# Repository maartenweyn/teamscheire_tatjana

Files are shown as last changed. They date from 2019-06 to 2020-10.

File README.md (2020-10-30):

# Team Scheire Tatjana - Tinnitus

Aflevering op VRTNu: [https://vrtnu.page.link/GqeyBG1gsRzztzNG9](https://vrtnu.page.link/GqeyBG1gsRzztzNG9)

Uitleg over de oplossing in deze podcast: [https://soundcloud.com/nerdlandmakertalk/09-maarten-weyn](https://soundcloud.com/nerdlandmakertalk/09-maarten-weyn)

# Geluidsmetingen

## 1. Wat is geluid?

**Geluid** is de **hoorbare verandering** van **luchtdruk** , of als je helemaal volledig wil zijn de verandering van de **dichtheid** van een **elastisch medium** , dat kan een **gas** zijn, een **vloeistof** of een **vaste** stof. En een geluidsbron veroorzaak verandering in de luchtdruk die zich in een golfbeweging door de lucht voortbewegen. Een luidspreker bijvoorbeeld zet een elektrisch signaal om in een beweging van een membraan. Die beweging zal dan een verandering in de luchtdruk veroorzaken.

Geluidsgolven tussen 20 Hz en 20 kHz, m.a.w. golven die 20 tot 20 000 keer per seconde bewegen kunnen door de mensen worden waargenomen. Boven 20 kHz hebben we wat we ultrasoon noemen.

Wist je dat geluid zich in lucht (bij 20°C en op zeeniveau) met ongeveer 343 m/s (of 1230 km/u) voortbeweegt, en in water van 20°C zelfs met 1482 m/s.

## 2. Wat is dan de geluidssterkte?

De **geluidsdruk** is het lokale drukverschil t.o.v. de atmosferische luchtdruk ten gevolge van een geluidsgolf. En dat wordt typisch in Pascal uitgedrukt.

Dit verschil wordt over een zeer kleine periode uitgemiddeld, men berekent de &quot;root mean square&quot; of de wortel van het gemiddelde van het kwadraat. Deze variatie is typisch zeer klein, de laagste waarde die nog hoorbaar is, is rond 2 \* 10-5 of 0.00002 Pa terwijl een explosie ongeveer 104 of 10000 kan zijn.

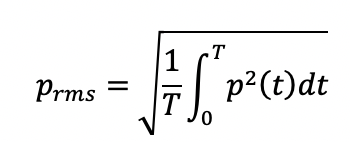
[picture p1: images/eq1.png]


Daarom gebruik met een logaritmes waarde om de geluidsruk uit te drukken en dat noemen het **geluidsniveau** of Sound Pressure Level (SPL) in dB:



Met p0 de referentieruk 2 x 10-5 Pa of 20 uPa, de gehoordrempel van een gemiddeld persoon bij een frequentie van 1000 Hz.

Dus deze waarde geeft een indicatie hoeveel keer het geluid luider is dan gehoordrempel.

## 3. Wat is een logaritme?

In het geval van een geluidsniveau wordt een logaritme gebruikt met grondtal 10. In dat geval is de logaritme van een getal het getal waartoe 10 moet worden verheven. de logaritme van 1000 is bijvoorbeeld 3 want 103 = 10 x 10 x 10 = 1000.

In het geval van het geluidsniveau berekenen we de logaritme van het aantal keer het geluid sterker is dan de gehoordrempel, en dat getal nog eens x 20.

## 4. Hoe kunnen we dat nu meten

We gaan dit meten met een MEMS microfoon. MEMS staat voor _microelectron-mechanical systems_ of hele kleine elektro-mechanische systemen. In een MEMS microfoon zit een zeer klein beweegbaar membraan, een klein gaatje (of meerdere) laten het toe dat de luchtdruk kan veranderen die door de geluidgolven worden veroorzaakt en een vaste structuur.

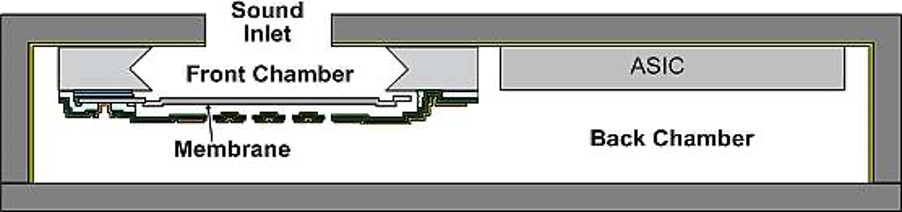
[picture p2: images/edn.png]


Diagram van een dwarssnede van een MEMS-microfoon (figuur van EDN)

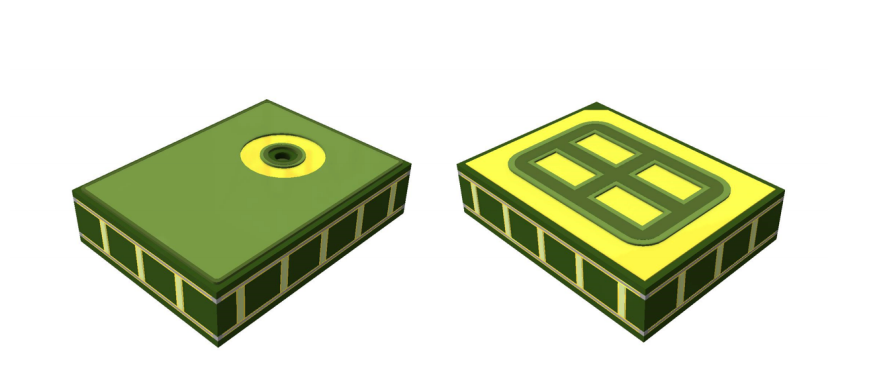
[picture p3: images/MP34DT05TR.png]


MP34DT05TR microfoon

Door de geluidgolven zal het membraan gaan bewegen en het verschil in capaciteit tussen het membraan en de vaste structuur wordt omgezet naar een elektrisch signaal.

In de chip van de MEMS-microfoon kan dit verschil in een spanning rechtstreeks worden doorgegeven naar een microcontroller (in analoge MEMS-microfoons) of in een digitale kan ze omgezet worden aar een PDM signaal.

Een PDM staat voor pulse density modulation. Bij PDM wordt een analoog signaal omgezet naar een binair signaal. In plaats van het signaal om te zetten naar codewoorden, komt bij PDM de relatieve dichtheid van de pulsen overeen met de amplitude van het analoge signaal.

0101101111111111111101101010010000000000000100010011011101111111111111011010100100000000000000100101

Vertegenwoordigd bvb



Figuur van Wikipedia (Kaldosh)

Het geluid wordt in dit geval 16000 keer per seconden gemeten. De microfoon is gekalibreerd en meet een waarde 1642 bij 94 dbA. Daarnaast meten we ook een root mean square gemiddelde in plaats van een dbFS (full scale meting) en we moeten dit nog corrigeren.

double leq = 3.0103+ 94 + 20 \* log10(sqrt(sumsquare / total\_samples) / 1642);

Nu voor we de samples gebruiken wordt de gemeten waarde nog gewogen naar de frequenties waarvoor het menselijk oor gevoeliger is. Zo worden bvb tonen onder de 1000 verzwakt. Een toon van 10 Hz wordt 70 keer zwakker gehoord dan een toon van 1000 Hz. Hoeveel dit niet helemaal correct is gebruiken we wel de dB(A) omdat de normen en wetgeving ook gebruik maakt van deze gewogen waarden.

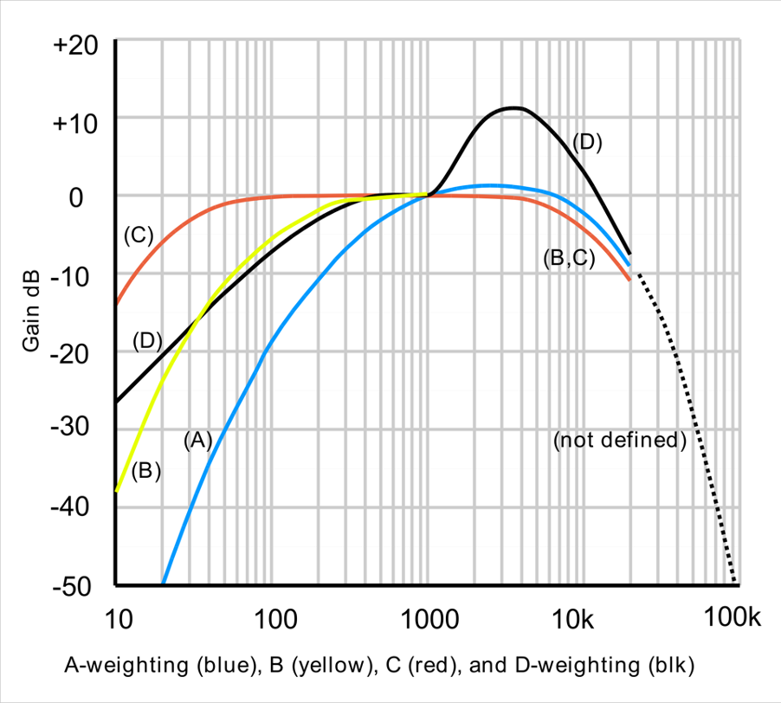
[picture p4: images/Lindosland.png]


Figuur van Lindosland at English Wikipedia

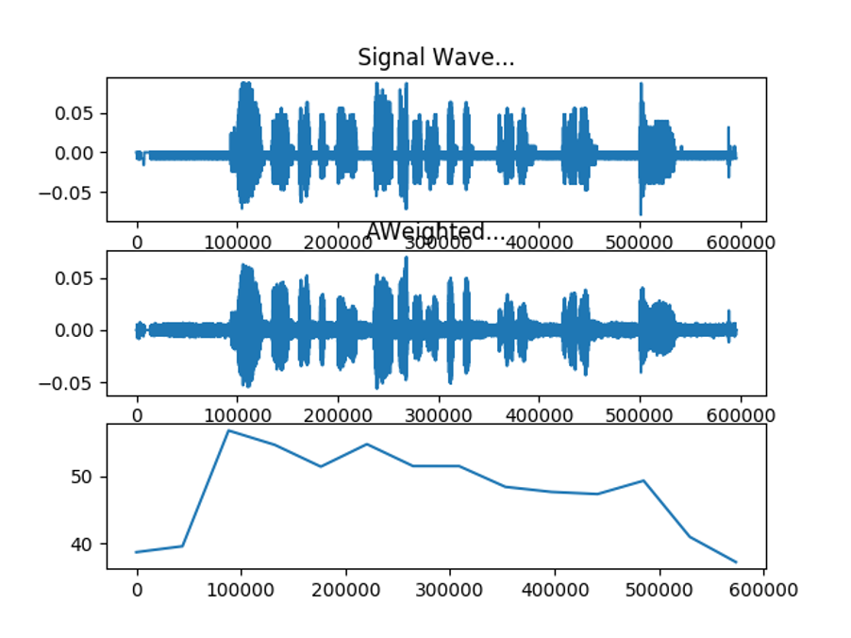
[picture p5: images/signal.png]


Nu kunnen we bijvoorbeeld per seconden meten wat het geluidsniveau is. Maar eigenlijk zijn we niet op zoek naar het geluidsniveau zelf, maar wel naar de geluidsdosis.

## 5. Wat is de geluidsdosis?

Een **geluidsdosis** is het gemiddelde geluidsniveau over een bepaalde (langere periode), bijvoorbeeld 8 uur of 24 uur. De WHO (wereld gezondheidsorganisatie) zegt dat deze normen voor 8u 80 dbA zijn en voor 24u 75 dbA.

Qua energieverbruik en dataopslag kunnen we uiteraard niet 8 u geluid gaan opnemen maar nemen we elke 10 seconden een sample van 1 seconde. Daarop bereken we het geluidsniveau. Daarna middelen we dit uit over 8u en 24u.

Je mag niet de gemiddeld van de dBA waarden nemen, dit zijn immers gemiddelde. Maar zetten de waardes eerst terug om naar de geluidsdruk en berekenen dan hoeveel % we reeds hebben ten opzichte van de herberekende waarde. Zo krijgen we 2 percentages die ook intuïtiever kunnen gebruikt worden door de gebruiker van het systeem.

# Wat staat er in de repo

* In **tizen** staat de oorspronkelijk ontwikkeling voor de Samsung Watch.
* In **hardware** het schema en PCB van de ontwikkelde wearble mee ontwikkeld door Kwinten Schram.
* In **3DModel** de stl van de gebruikte behuizing
* In **Arduino** een aantal test applicaties
* In **cordova** de cordova applicatie voor iOS
* In **Firmware** de code voor de wearable

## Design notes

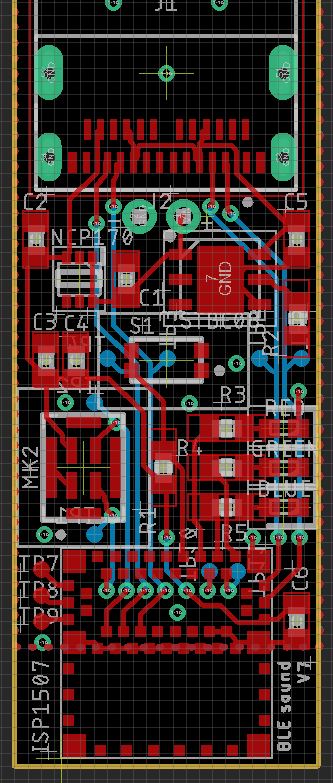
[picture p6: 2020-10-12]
hardware/brd1.JPG

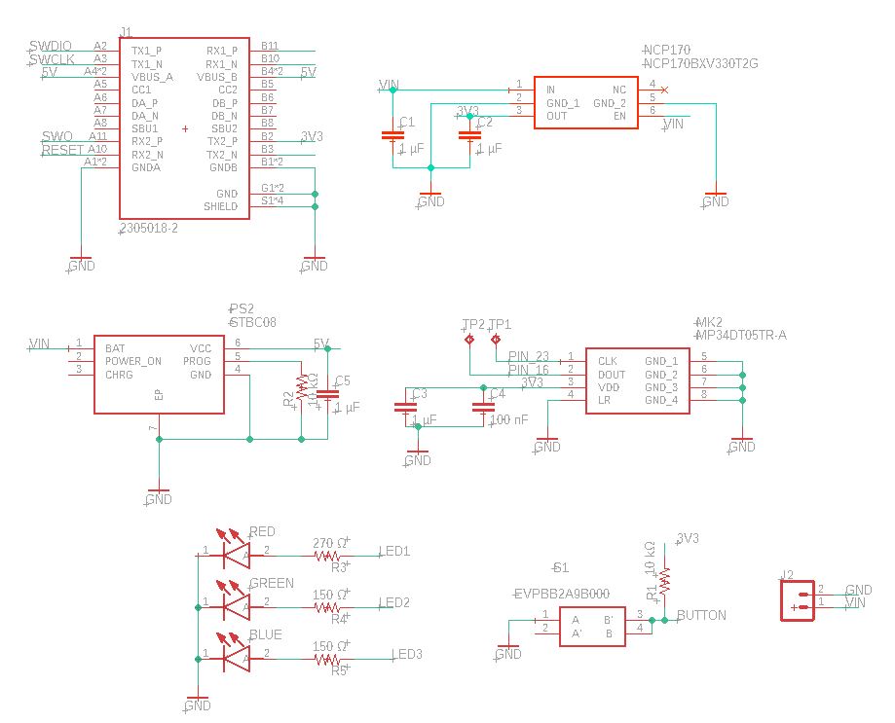
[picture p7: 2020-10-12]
hardware/sch1.JPG

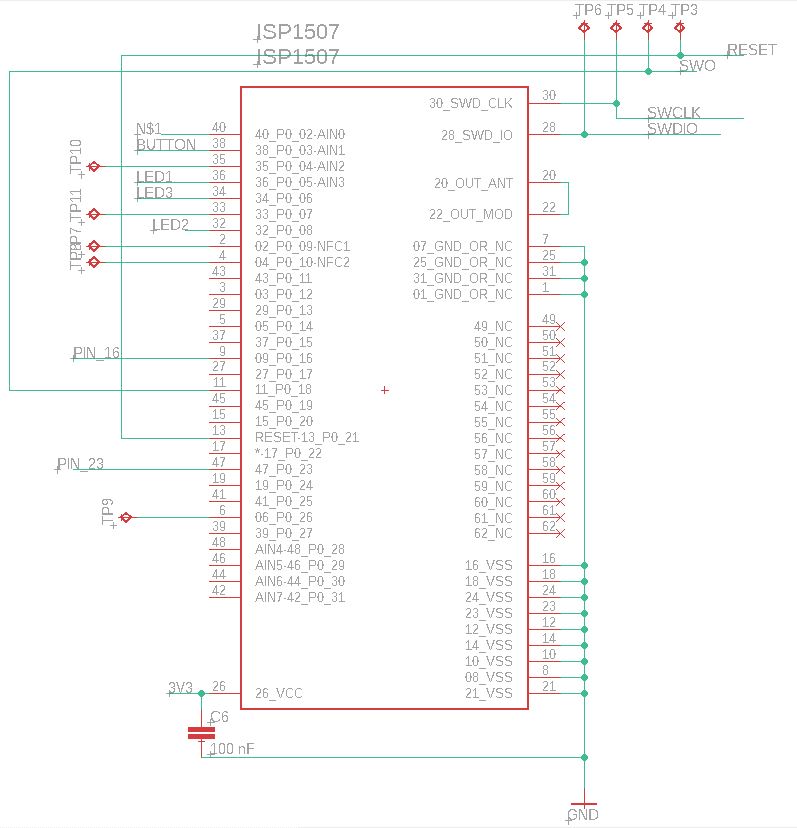
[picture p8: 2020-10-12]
hardware/sch2.JPG

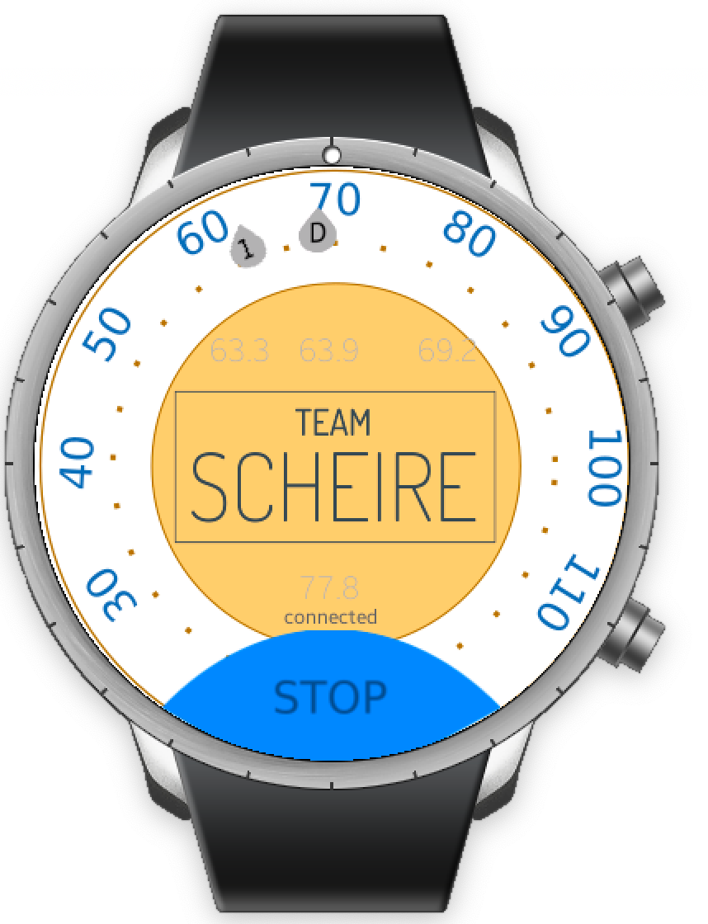
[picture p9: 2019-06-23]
images/screenshot2.png

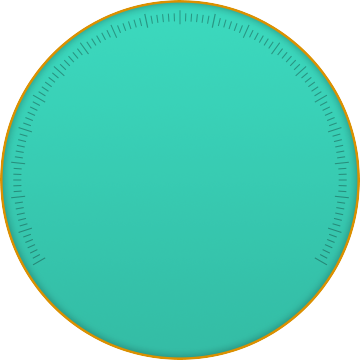
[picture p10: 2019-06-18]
tizen/workspace/TatySoundWebViewer/image/board_run_bg.png

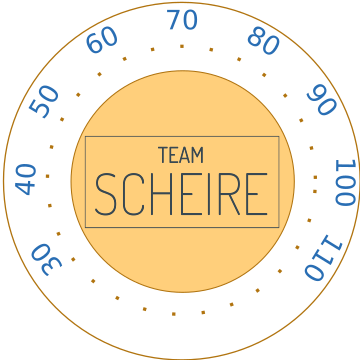
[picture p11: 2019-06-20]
tizen/workspace/TatySoundViewer/res/images/board_bg.png

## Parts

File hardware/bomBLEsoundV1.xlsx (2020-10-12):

Part | Value | Device | Package | Description | MANUFACTURER_PART_NUMBER | FARNELL | Mouser | MOUSER_PART_NUMBER | MOUSER_PRICE-STOCK | MP | RS_PART_NUMBER | RS_PRICE-STOCK | TE_PURCHASE_URL
C1 | 1 µF | SPARKFUN_CAP0402-CAP | 1 µf 0402 | Capacitor |  | 1327658
C2 | 1 µF | SPARKFUN_CAP0402-CAP | 1 µf 0402 | Capacitor
C3 | 1 µF | SPARKFUN_CAP0402-CAP | 1 µf 0402 | Capacitor
C4 | 100 nF | SPARKFUN_CAP0402-CAP | 100 nF 0402 | Capacitor |  | 1867948
C5 | 1 µF | SPARKFUN_CAP0402-CAP | 1 µf 0402 | Capacitor
C6 | 100 nF | SPARKFUN_CAP0402-CAP | 100 nF 0402 | Capacitor
R1 | 10 kΩ | SPARKFUN_RESISTOR0402-RES | 10 kΩ 0402 | Resistor |  | 1469669
R2 | 10 kΩ | SPARKFUN_RESISTOR0402-RES | 10 kΩ 0402 | Resistor
R3 | 270 Ω | SPARKFUN_RESISTOR0402-RES | 270 Ω 0402 | Resistor |  | 9239162
R4 | 150 Ω | SPARKFUN_RESISTOR0402-RES | 150 Ω 0402 | Resistor |  | 1652754
R5 | 150 Ω | SPARKFUN_RESISTOR0402-RES | 150 Ω 0402 | Resistor
5988A20107F-RED | 5988A20107F | 5988A20107F | 402 | 5988A20107F - LED, Red, SMD, 0402, 5 mA, 1.8 V, 625 nm | 5988A20107F | 3131546
5988A80107F-GREEN | 5988A80107F | 5988A80107F | 402 | 5988A80107F - LED, Green, SMD, 0402, 5 mA, 2.5 V, 528 nm | 5988A80107F | 3131550
5988A90107F-BLUE | 5988A90107F | 5988A90107F | 402 | 5988A90107F - LED, Blue, SMD, 0402, 5 mA, 2.5 V, 470 nm | 5988A90107F | 3131551
S1 | EVPBB2A9B000 | EVPBB2A9B000 | EVPBB2A9B000 | IP67 Push Plate Tact Switch, SPST 20 mA @ 15 V dc 0.7 (Dia.)mm Surface Mount | EVPBB2A9B000 | 2831725 |  |  |  |  | 1250187P | http://uk.rs-online.com/web/p/products/1250187P
J1 | 2305018-2 | 2305018-2 | TE_2305018-2 | TYPE C Right Angle Sealable SMT IPX8 3.1 GEN 2 Wire to Board USB | 2305018-2 | 2896219 |  |  |  | 2305018-2 |  |  | https://www.te.com/usa-en/product-2305018-2.html?te_bu=Cor&te_type=disp&elqCampaignId=32493
MK2 | MP34DT05TR-A | MP34DT05TR-A | MP34DT05TRA | STMICROELECTRONICS - MP34DT05TR-A - MEMS MICROPHONE, 3.6V, HCLGA-4 | MP34DT05TR-A | 2851942 |  | 511-MP34DT05TR-A | https://www.mouser.com/Search/Refine.aspx?Keyword=511-MP34DT05TR-A
NCP170BXV310T2G | NCP170BXV310T2G | NCP170BXV310T2G | SOTFL50P160X60-6N | LDO Voltage Regulators ULTRA-LOW IQ 150 MA | NCP170BXV310T2G | 2706298 |  | 863-NCP170BXV330T2G | https://www.mouser.com/Search/Refine.aspx?Keyword=863-NCP170BXV330T2G
PS2 | STBC08PMR | STBC08PMR | SON95P300X300X100-7N | STMicroelectronics STBC08PMR, Battery Charger, 800mA, 6-Pin DFN | STBC08PMR | 2762712 |  |  |  |  | 1655533
ISP1507 | ISP1507 | ISP1507 | ISP1507 | ISP1507 BLE Module | ISP1507-AX-RS |  | 359-ISP1507-AX-RS

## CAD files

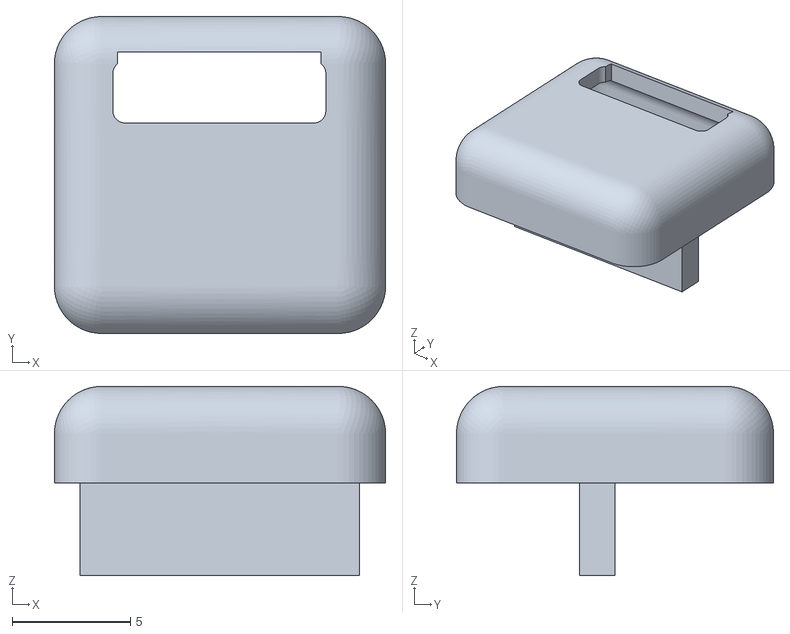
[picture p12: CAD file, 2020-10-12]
3dmodel/dop_usb mini.stl
14.0 x 13.4 x 8.00

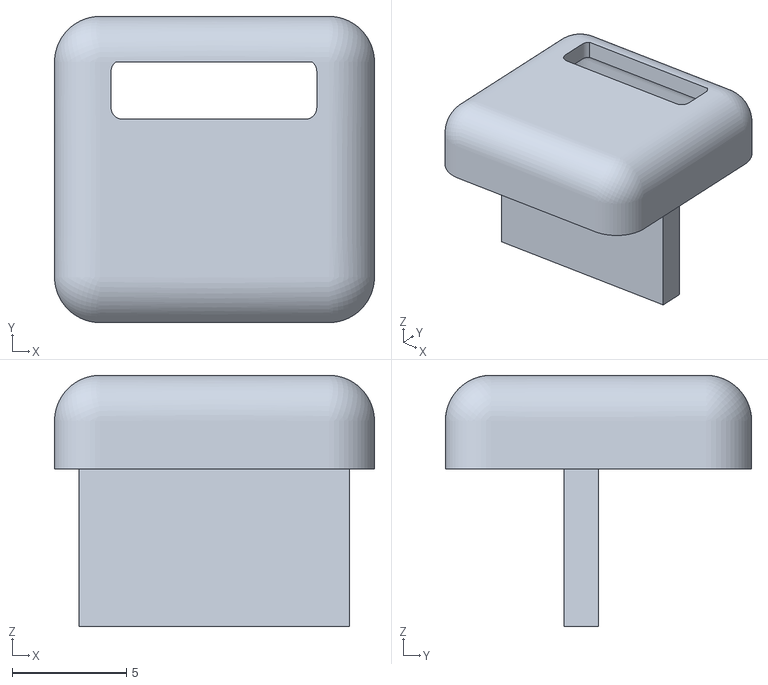
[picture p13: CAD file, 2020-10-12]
3dmodel/dop_usbc.stl
14.0 x 13.4 x 11.0

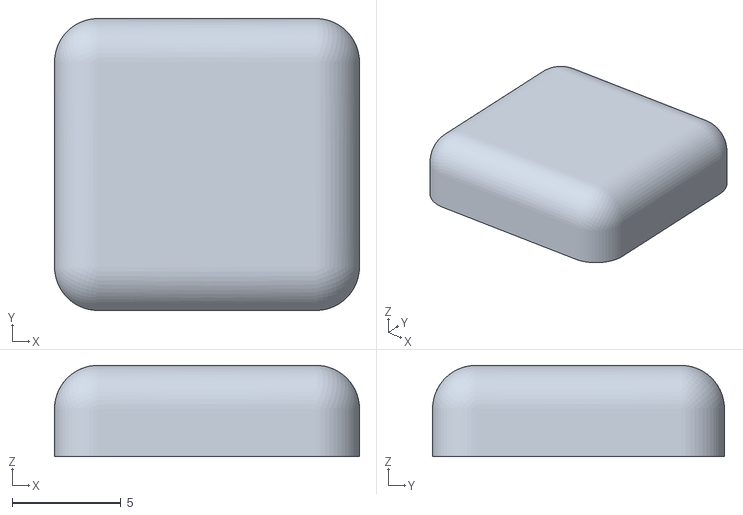
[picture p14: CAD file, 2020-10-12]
3dmodel/Body2_simple.stl
14.0 x 13.4 x 4.19

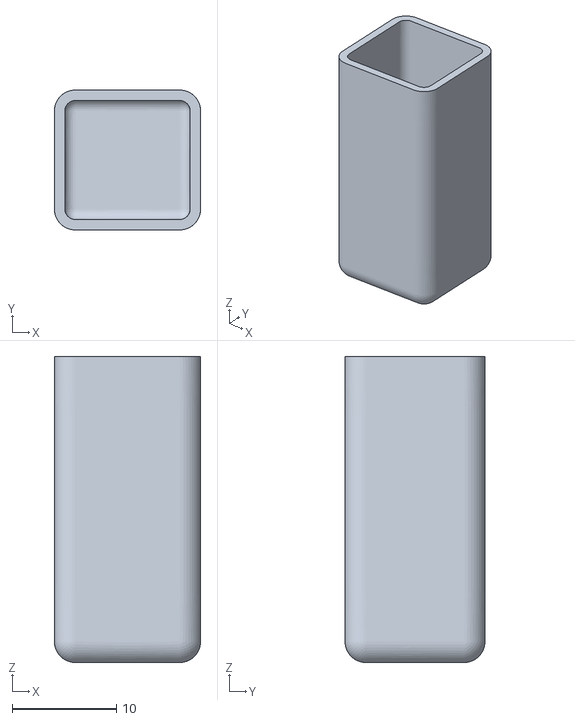
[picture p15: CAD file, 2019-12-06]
3dmodel/part1.stl
14.0 x 13.4 x 29.3

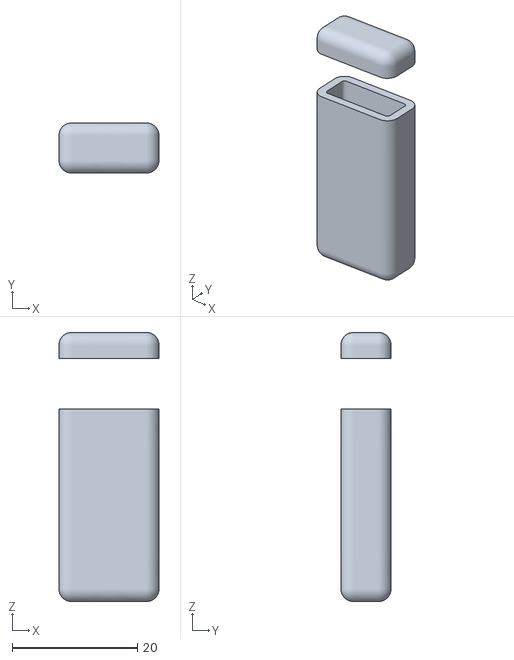
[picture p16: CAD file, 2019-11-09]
3dmodel/Tatysound_dummy v0.stl
16.0 x 8.00 x 43.0

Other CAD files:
3dmodel/Tatysound_enclosure v6.f3d

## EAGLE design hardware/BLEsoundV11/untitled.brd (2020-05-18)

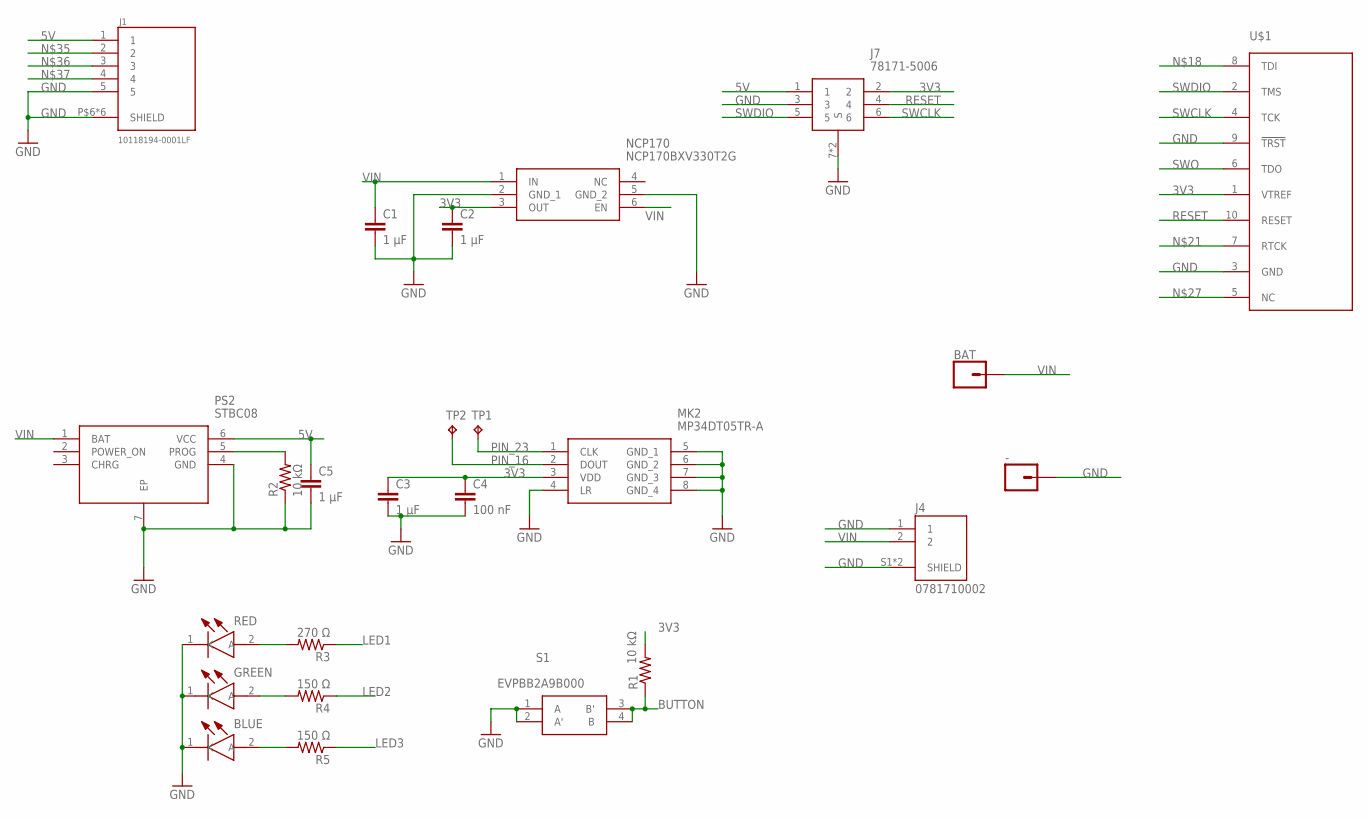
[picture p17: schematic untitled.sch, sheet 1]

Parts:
-: CONN_01; 1X01
BAT: CONN_01; 1X01
BLUE: 150040GS73220; LEDC1005X50N
C1, C2, C3, C5: 1 µF; SPARKFUN_0402-CAP
C4: 100 nF; SPARKFUN_0402-CAP
GREEN: 150040GS73220; LEDC1005X50N
J1: 10118194-0001LF; AMPHENOL_10118194-0001LF
J4: 0781710002; MOLEX_0781710002
J7: 78171-5006
MK2: MP34DT05TR-A; MP34DT05TRA
NCP170: NCP170BXV330T2G; SOTFL50P160X60-6N
PS2: STBC08; SON95P300X300X100-7N
R1, R2: 10 kΩ; SPARKFUN_0402-RES
R3: 270 Ω; SPARKFUN_0402-RES
R4, R5: 150 Ω; SPARKFUN_0402-RES
RED: 150040GS73220; LEDC1005X50N
S1: EVPBB2A9B000
TP1, TP2: TPTP06R; TP06R
U$1: TC2050-NL-MCP-NL; TC2030-MCP-NL

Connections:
3V3: C2.1, C3.1, C4.1, J7.2, MK2.3 (VDD), NCP170.3 (OUT), R1.2, U$1.1 (VTREF); also elsewhere on the board
5V: C5.1, J1.1, J7.1, PS2.6 (VCC)
BUTTON: R1.1, S1.3 (B'), S1.4 (B); also elsewhere on the board
GND: -.1, BLUE.1 (K), C1.2, C2.2, C3.2, C4.2, C5.2, GREEN.1 (K), J1.5, J1.P$6 (SHIELD), J1.P$7 (SHIELD), J1.P$8 (SHIELD), J1.P$9 (SHIELD), J1.P$10 (SHIELD), J1.P$11 (SHIELD), J4.1, J4.S1 (SHIELD), J4.S2 (SHIELD), J7.3, J7.7 (S), J7.8 (S), MK2.4 (LR), MK2.5 (GND_1), MK2.6 (GND_2), MK2.7 (GND_3), MK2.8 (GND_4), NCP170.2 (GND_1), NCP170.5 (GND_2), PS2.4 (GND), PS2.7 (EP), R2.1, RED.1 (K), S1.1 (A), S1.2 (A'), U$1.3 (GND), U$1.9 (!TRST); also elsewhere on the board
LED1: R3.1; also elsewhere on the board
LED2: R4.1; also elsewhere on the board
LED3: R5.1; also elsewhere on the board
unnamed: R3.2, RED.2 (A)
unnamed: GREEN.2 (A), R4.2
unnamed: BLUE.2 (A), R5.2
unnamed: PS2.5 (PROG), R2.2
PIN_16: MK2.2 (DOUT), TP2.TP; also elsewhere on the board
PIN_23: MK2.1 (CLK), TP1.TP; also elsewhere on the board
RESET: J7.4, U$1.10 (RESET); also elsewhere on the board
SWCLK: J7.6, U$1.4 (TCK); also elsewhere on the board
SWDIO: J7.5, U$1.2 (TMS); also elsewhere on the board
SWO: U$1.6 (TDO); also elsewhere on the board
VIN: BAT.1, C1.1, J4.2, NCP170.1 (IN), NCP170.6 (EN), PS2.1 (BAT)

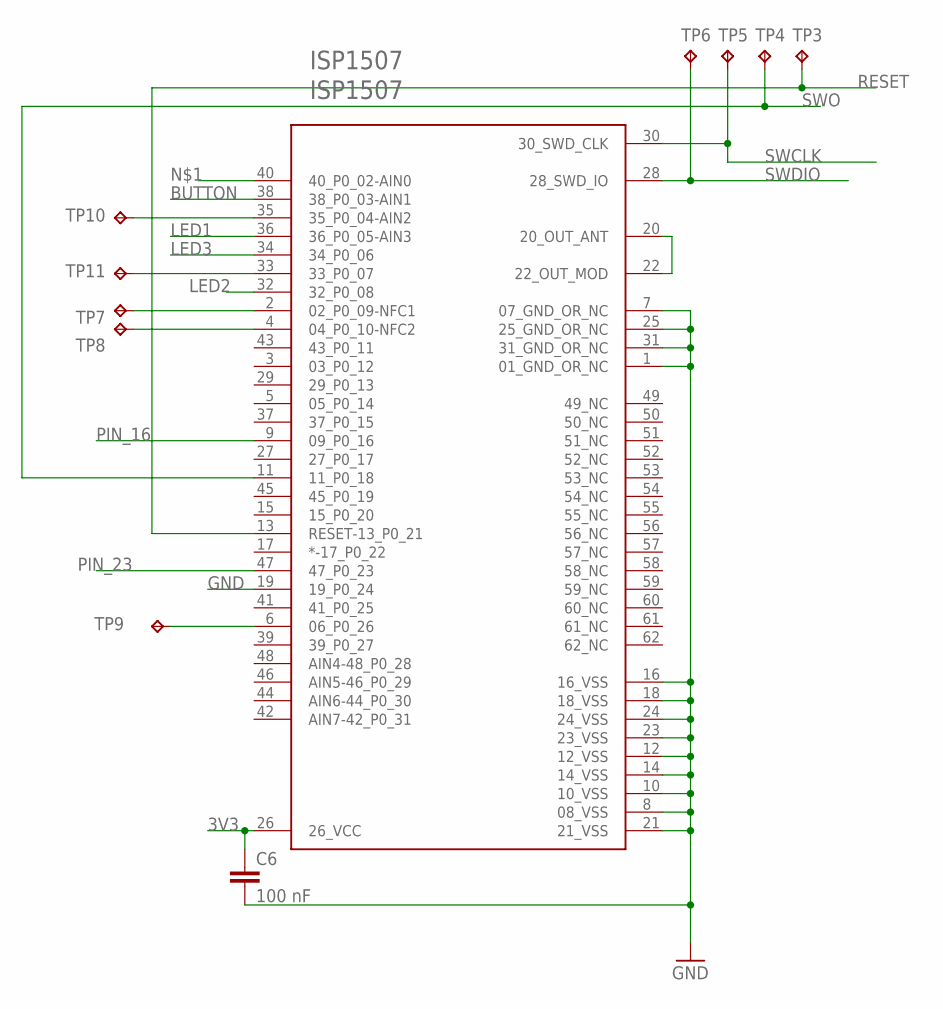
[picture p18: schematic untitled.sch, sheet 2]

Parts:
C6: 100 nF; SPARKFUN_0402-CAP
ISP1507: ISP1507
TP3, TP4, TP5, TP6, TP7, TP8, TP9, TP10, TP11: TPTP06R; TP06R

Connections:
3V3: C6.1, ISP1507.26 (26_VCC); also elsewhere on the board
BUTTON: ISP1507.38 (38_P0_03-AIN1); also elsewhere on the board
GND: C6.2, ISP1507.1 (01_GND_OR_NC), ISP1507.7 (07_GND_OR_NC), ISP1507.8 (08_VSS), ISP1507.10 (10_VSS), ISP1507.12 (12_VSS), ISP1507.14 (14_VSS), ISP1507.16 (16_VSS), ISP1507.18 (18_VSS), ISP1507.19 (19_P0_24), ISP1507.21 (21_VSS), ISP1507.23 (23_VSS), ISP1507.24 (24_VSS), ISP1507.25 (25_GND_OR_NC), ISP1507.31 (31_GND_OR_NC); also elsewhere on the board
LED1: ISP1507.36 (36_P0_05-AIN3); also elsewhere on the board
LED2: ISP1507.32 (32_P0_08); also elsewhere on the board
LED3: ISP1507.34 (34_P0_06); also elsewhere on the board
unnamed: ISP1507.6 (06_P0_26), TP9.TP
unnamed: ISP1507.2 (02_P0_09-NFC1), TP7.TP
unnamed: ISP1507.4 (04_P0_10-NFC2), TP8.TP
unnamed: ISP1507.35 (35_P0_04-AIN2), TP10.TP
unnamed: ISP1507.33 (33_P0_07), TP11.TP
unnamed: ISP1507.20 (20_OUT_ANT), ISP1507.22 (22_OUT_MOD)
PIN_16: ISP1507.9 (09_P0_16); also elsewhere on the board
PIN_23: ISP1507.47 (47_P0_23); also elsewhere on the board
RESET: ISP1507.13 (RESET-13_P0_21), TP3.TP; also elsewhere on the board
SWCLK: ISP1507.30 (30_SWD_CLK), TP5.TP; also elsewhere on the board
SWDIO: ISP1507.28 (28_SWD_IO), TP6.TP; also elsewhere on the board
SWO: ISP1507.11 (11_P0_18), TP4.TP; also elsewhere on the board

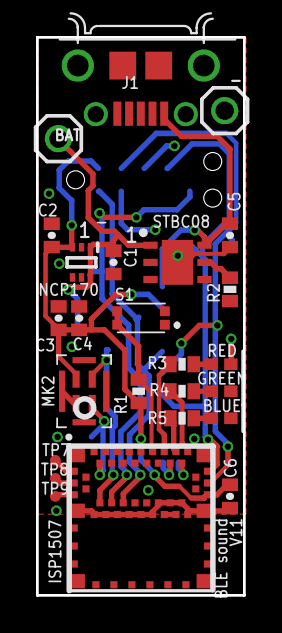
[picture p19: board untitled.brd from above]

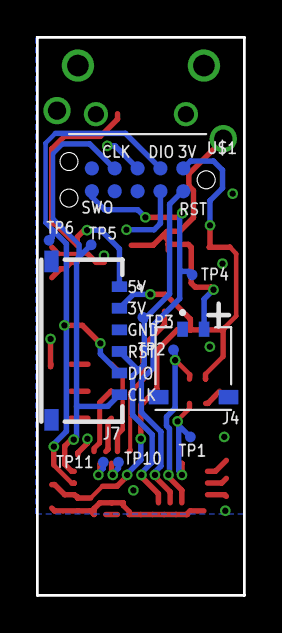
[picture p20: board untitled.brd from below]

Board: 2 copper layers, 11.5 x 31.0 mm, 36 parts (11 on the bottom side), 24 nets.

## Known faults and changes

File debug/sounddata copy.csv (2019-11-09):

0 | -4289 | 0x20003570
1 | -4288 | 0x20003574
2 | -4286 | 0x20003578
3 | -4286 | 0x2000357c
4 | -4290 | 0x20003580
5 | -4292 | 0x20003584
6 | -4290 | 0x20003588
7 | -4286 | 0x2000358c
8 | -4287 | 0x20003590
9 | -4289 | 0x20003594
10 | -4286 | 0x20003598
11 | -4286 | 0x2000359c
12 | -4287 | 0x200035a0
13 | -4286 | 0x200035a4
14 | -4289 | 0x200035a8
15 | -4290 | 0x200035ac
16 | -4289 | 0x200035b0
17 | -4290 | 0x200035b4
18 | -4293 | 0x200035b8
19 | -4293 | 0x200035bc
20 | -4293 | 0x200035c0
21 | -4294 | 0x200035c4
22 | -4296 | 0x200035c8
23 | -4295 | 0x200035cc
24 | -4296 | 0x200035d0
25 | -4301 | 0x200035d4
26 | -4303 | 0x200035d8
27 | -4303 | 0x200035dc
28 | -4301 | 0x200035e0
29 | -4303 | 0x200035e4
30 | -4306 | 0x200035e8
31 | -4305 | 0x200035ec
32 | -4306 | 0x200035f0
33 | -4306 | 0x200035f4
34 | -4308 | 0x200035f8
35 | -4302 | 0x200035fc
36 | -4298 | 0x20003600
37 | -4300 | 0x20003604
38 | -4302 | 0x20003608
39 | -4306 | 0x2000360c
40 | -4306 | 0x20003610
41 | -4303 | 0x20003614
42 | -4304 | 0x20003618
43 | -4307 | 0x2000361c
44 | -4309 | 0x20003620
45 | -4307 | 0x20003624
46 | -4305 | 0x20003628
47 | -4306 | 0x2000362c
48 | -4306 | 0x20003630
49 | -4305 | 0x20003634
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

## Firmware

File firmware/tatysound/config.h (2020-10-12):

#include <ble_types.h>

#include <app_timer.h>

#define ODR 200

#define ACC_TIMER_INTERVAL              1000/ODR                       /**< interval (msecs). */

#define ACC_LIST_SIZE 40 // restricted by max size of ble

#define I2S_BUFFER_SIZE     2000
#define SHORT_SAMPLE        16000
#define SKIP_BUFFERS        1
#define SAMPLE_RATE   16000//15650
#define CLOCK_PERIOD        16000000/(64*SAMPLE_RATE) 
#define MAX_BLE_DATA  1440
#define BLE_DATA_FREE  60 //if buffer full free 1 hour
#define MAX_BLE_DATA_THRESHOLD  0 //50

#define SOUND_TIMER_INTERVAL_SEC  10
#define SOUND_TIMER_INTERVAL  SOUND_TIMER_INTERVAL_SEC*1000

//PCM 
#define CONFIG_IO_PDM_CLK		23
#define CONFIG_IO_PDM_DATA		16
//#define CONFIG_IO_PDM_DATA		26

#define CONFIG_AUDIO_PDM_GAIN 		0x38
#define CONFIG_AUDIO_FRAME_SIZE_BYTES   64
#define CONFIG_AUDIO_FRAME_SIZE_SAMPLES 64
#define CONFIG_PDM_FRAME_SIZE_SAMPLES	64
#define CONFIG_AUDIO_FRAME_BUFFERS 	16

#define SOUND_BUFFER_SIZE     2000

// ADUIO PROCESSING
#define MIC_OFFSET_DB     3.0103    // Default offset (sine-wave RMS vs. dBFS)
#define MIC_REF_DB        94.0      // dB(SPL)
  #define MIC_REF_AMPL      1642 //Amplitude at 94dB(SPL) (-26dBFS from datasheet, i.e. (2^15-1)*10^(-26/20) )
//#define MIC_REF_AMPL      6569 //Amplitude at 94dB(SPL) (-26dBFS from datasheet, i.e. (2^17-1)*10^(-26/20) )
//#define MIC_REF_AMPL  0.050118723362727

// BLE

#define APP_BLE_CONN_CFG_TAG            1                                           /**< A tag identifying the SoftDevice BLE configuration. */
#define APP_BLE_OBSERVER_PRIO           3                                           /**< Application's BLE observer priority. You shouldn't need to modify this value. */

#define DEVICE_NAME                     "TatySound"                                    /**< Name of device. Will be included in the advertising data. */
#define NUS_SERVICE_UUID_TYPE           BLE_UUID_TYPE_VENDOR_BEGIN                  /**< UUID type for the Nordic UART Service (vendor specific). */

#define MIN_CONN_INTERVAL               MSEC_TO_UNITS(20, UNIT_1_25_MS)             /**< Minimum acceptable connection interval (20 ms), Connection interval uses 1.25 ms units. */
#define MAX_CONN_INTERVAL               MSEC_TO_UNITS(75, UNIT_1_25_MS)             /**< Maximum acceptable connection interval (75 ms), Connection interval uses 1.25 ms units. */
#define SLAVE_LATENCY                   0                                           /**< Slave latency. */
#define CONN_SUP_TIMEOUT                MSEC_TO_UNITS(4000, UNIT_10_MS)             /**< Connection supervisory timeout (4 seconds), Supervision Timeout uses 10 ms units. */
#define FIRST_CONN_PARAMS_UPDATE_DELAY  APP_TIMER_TICKS(5000)                       /**< Time from initiating event (connect or start of notification) to first time sd_ble_gap_conn_param_update is called (5 seconds). */
#define NEXT_CONN_PARAMS_UPDATE_DELAY   APP_TIMER_TICKS(30000)                      /**< Time between each call to sd_ble_gap_conn_param_update after the first call (30 seconds). */
#define MAX_CONN_PARAMS_UPDATE_COUNT    3                                           /**< Number of attempts before giving up the connection parameter negotiation. */

#define APP_BLE_OBSERVER_PRIO           3                                           /**< Application's BLE observer priority. You shouldn't need to modify this value. */

#define APP_ADV_INTERVAL                64                                          /**< The advertising interval (in units of 0.625 ms. This value corresponds to 40 ms). */
#define APP_ADV_DURATION                10//18000                                       /**< The advertising duration (180 seconds) in units of 10 milliseconds. */

#define SLOW_APP_ADV_INTERVAL           1600   //1000 ms * 1.6
#define SLOW_APP_ADV_TIMEOUT_IN_SECONDS 0


// Buttons
#define BUTTON1 3

// LEDS

#define LED1  5
#define LED2  8
#define LED3  6

#define LED_RED LED1
#define LED_GREEN LED2
#define LED_BLUE LED3

#define LED_INDICATE_SENT_OK               0
#define LED_INDICATE_SEND_ERROR            0
#define LED_INDICATE_RCV_OK                0
#define LED_INDICATE_RCV_ERROR             0
#define LED_INDICATE_CONNECTED             LED_BLUE
#define LED_INDICATE_BONDING               0
#define LED_INDICATE_ADVERTISING_DIRECTED  0
#define LED_INDICATE_ADVERTISING_SLOW      0
#define LED_INDICATE_ADVERTISING_WHITELIST 0
#define LED_INDICATE_ADVERTISING  0

#define LED_INDICATE_TX  0


#define RED 1
#define GREEN 2
#define BLUE  4
#define WHITE 7

#define RED_ID   0
#define GREEN_ID 1
#define BLUE_ID  2


#define LED_BRIGHTNESS  10


#define ADVERTISING_LED_ON_INTERVAL             100
#define ADVERTISING_LED_OFF_INTERVAL            4900

#define CONNECTED_LED_ON_INTERVAL               100
#define CONNECTED_LED_OFF_INTERVAL              3000

#define ADVERTISING_DIRECTED_LED_ON_INTERVAL   200
#define ADVERTISING_DIRECTED_LED_OFF_INTERVAL  200

#define ADVERTISING_WHITELIST_LED_ON_INTERVAL  200
#define ADVERTISING_WHITELIST_LED_OFF_INTERVAL 800

#define ADVERTISING_SLOW_LED_ON_INTERVAL       400
#define ADVERTISING_SLOW_LED_OFF_INTERVAL      4000

#define BONDING_INTERVAL                       100

#define SENT_OK_INTERVAL                       100
#define SEND_ERROR_INTERVAL                    500

#define RCV_OK_INTERVAL                        100
#define RCV_ERROR_INTERVAL                     500

#define ALERT_INTERVAL                         200

#define LIGHT_BUTTON_CHANGE_INTERVAL            1000
#define BUTTON_TIMEOUT_INTERVAL                 10000
#define BUTTON_ACK_FLASH_INTERVAL               500

extern uint8_t sleep_status;

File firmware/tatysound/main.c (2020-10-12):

#include "app_timer.h"
#include "app_uart.h"
#include "app_util_platform.h"
#include "ble_advdata.h"
#include "ble_advertising.h"
#include "ble_conn_params.h"
#include "ble_hci.h"
#include "ble_nus.h"
#include "bsp_btn_ble.h"
#include "nordic_common.h"
#include "nrf.h"
#include "nrf_ble_gatt.h"
#include "nrf_sdh.h"
#include "nrf_sdh_ble.h"
#include "nrf_sdh_soc.h"
#include <stdint.h>
#include <string.h>

#include "math.h"
#include "nrf_drv_pdm.h"

#include "app_pwm.h"

#include "i2c.h"
#include "lp55231.h"
#include "nrf_delay.h"
#include "nrf_drv_twi.h"
#include "nrf_drv_i2s.h"

#include "ble_app.h"
#include "config.h"
#include "lsm303_agr.h"
#include "battery.h"

#include "nrf_log.h"
#include "nrf_log_ctrl.h"
#include "nrf_log_default_backends.h"

#include "nrfx_pdm.h"

#include <nrf_drv_gpiote.h>
#include <nrf_pwr_mgmt.h>

APP_TIMER_DEF(m_button_timer_id);
APP_TIMER_DEF(m_light_timer_id);

extern nrf_twi_mngr_t m_nrf_twi_mngr;
static bsp_indication_t m_stable_state = BSP_INDICATE_IDLE;
static bool m_leds_clear = false;
static bool m_alert_on = false;
APP_TIMER_DEF(m_app_leds_tmr);
APP_TIMER_DEF(m_app_tx_tmr);
APP_TIMER_DEF(m_sound_tmr);

#define on(led)     nrf_gpio_pin_set(led)
#define off(led)    nrf_gpio_pin_clear(led)
#define toggle(led)    nrf_gpio_pin_toggle(led)

typedef struct {
  uint8_t type;
  uint32_t time;
  uint16_t cdBSPL;
} sound_data_element_t;

sound_data_element_t ble_data[MAX_BLE_DATA];
uint16_t ble_data_size = 0;

static volatile uint8_t led_status[8][3] = {0};
static volatile bool transmitting = false;
static uint8_t led_driver_status[3] = {0};
static uint8_t light_brightness = 50;
static uint8_t front_light_status = 0;

static uint32_t time_stamp = 0;
static uint32_t prev_stamp = 0;

static uint8_t front_light_brightness_changed = 0;
static uint8_t button_pushed = 0;

uint32_t app_indication_set(bsp_indication_t indicate);
static void app_leds_timer_handler(void *p_context);
static void app_tx_timer_handler(void *p_context);
static void sound_timer_handler(void *p_context);
void set_led(uint8_t led_nr, uint8_t color, uint8_t brightness);
void set_front_light(uint8_t status);
static uint32_t send_data_to_ble(uint8_t *data, uint16_t length);
void set_all_leds_color(uint8_t color, uint8_t brightness);

uint8_t sleep_status = 0; // 0 can go to sleep,  1 keep awake
extern uint8_t ble_state;

static bool first_sample = true;

                                                                           
//static uint32_t m_buffer_rx[];
//static int32_t soundbuffer[SHORT_SAMPLE];
static int16_t soundbuffer[3][SOUND_BUFFER_SIZE];
static uint16_t buffer_offset = 0;
static uint8_t buffer_index = 0;
static volatile bool sampling_running = true;

static nrfx_pdm_config_t pdm_cfg = NRFX_PDM_DEFAULT_CONFIG(CONFIG_IO_PDM_CLK, CONFIG_IO_PDM_DATA);

static volatile int soundbuffer_position = -SKIP_BUFFERS;
static double prev_avg = 0;
static volatile bool parse_sound = false;

static volatile uint8_t     pwm_ready = 0;                                                                       // A PWM ready status

static void pdm_event_handler(nrfx_pdm_evt_t const * const p_evt);

uint32_t start_sound_measurement() {

  NRF_LOG_DEBUG("Starting pdm");
  
  //app_indication_set(BSP_INDICATE_USER_STATE_2);

  //buffer_index = 0;
  int32_t err_code = 0;
  //uint32_t err_code = nrfx_pdm_buffer_set(soundbuffer[buffer_index], SOUND_BUFFER_SIZE);
  //APP_ERROR_CHECK(err_code);

 // err_code = nrfx_pdm_start();

  err_code = nrfx_pdm_init(&pdm_cfg, pdm_event_handler);

    if (err_code != 0) {
    NRF_LOG_INFO("cannot nrfx_pdm_init\n");
  }    

  err_code = nrfx_pdm_start();
  
  if (err_code != 0) {
    NRF_LOG_INFO("cannot nrfx_pdm_start\n");
  }    

  if (err_code == NRFX_SUCCESS)
    sampling_running = true;


  return err_code;

}

void stop_sound_measurement() {

  NRF_LOG_DEBUG("Stopping pdm");

  nrfx_pdm_uninit();

  sampling_running = false;
}

/**@brief Function for handling the data from the Nordic UART Service.
 *
 * @details This function will process the data received from the Nordic UART BLE Service and send
 *          it to the UART module.
 *
 * @param[in] p_nus    Nordic UART Service structure.
 * @param[in] p_data   Data to be send to UART module.
 * @param[in] length   Length of the data.
 */
/**@snippet [Handling the data received over BLE] */
static void nus_data_handler(ble_nus_evt_t *p_evt) {
  NRF_LOG_DEBUG("nus_data_handler %d", p_evt->type);
  if (p_evt->type == BLE_NUS_EVT_RX_DATA) {
    uint32_t err_code;

    NRF_LOG_DEBUG("Received data from BLE NUS., length %d:", p_evt->params.rx_data.length);
    NRF_LOG_HEXDUMP_DEBUG(p_evt->params.rx_data.p_data, p_evt->params.rx_data.length);

    uint8_t type = p_evt->params.rx_data.p_data[2];
    uint8_t length = p_evt->params.rx_data.p_data[3];

    switch (type) {
      case 1:
      {
        uint32_t* ts = (uint32_t*) &p_evt->params.rx_data.p_data[4];
        NRF_LOG_INFO("Received time: %d", *ts);
        time_stamp = *ts;
        break;
      }
      default:
        NRF_LOG_ERROR("Unkown data type received: %d", type);
    }

  }
}

/* BUTTONS */

void in_pin_handler(nrf_drv_gpiote_pin_t pin, nrf_gpiote_polarity_t action) {
  //nrf_drv_gpiote_out_toggle(PIN_OUT);
  int32_t pin_state = nrf_gpio_pin_read(pin);
  NRF_LOG_INFO("in_pin_handler %d - %d / %d", pin, action, pin_state);

//   if (pin_state == 0) {
//      set_all_leds_color(GREEN, 50);
//    } else {
//      set_all_leds_color(GREEN, 0);
//    }
}

ret_code_t init_buttons() {
  ret_code_t err_code;

  err_code = nrfx_gpiote_init();
  APP_ERROR_CHECK(err_code);

  nrf_drv_gpiote_in_config_t in_config = GPIOTE_CONFIG_IN_SENSE_TOGGLE(true);
  in_config.pull = NRF_GPIO_PIN_PULLUP;

  err_code = nrf_drv_gpiote_in_init(BUTTON1, &in_config, in_pin_handler);
  APP_ERROR_CHECK(err_code);

  nrf_drv_gpiote_in_event_enable(BUTTON1, true);

  return err_code;
}

/* LEDS */


static uint32_t send_data_to_ble(uint8_t *data, uint16_t length) {
  NRF_LOG_INFO("send_data_to_ble");

  uint32_t err_code;

  do {
    err_code = send_data(data, length);
    if (err_code != NRF_ERROR_BUSY) {
      if (err_code != NRF_SUCCESS) {
        NRF_LOG_INFO("send_data error %d\n", err_code);
      }
    }
  } while (err_code == NRF_ERROR_BUSY);

  return err_code;
}

/* TIMERS */

/**@brief Function for initializing the timer module and the application timers
 */
static void timers_init(void) {
  // Initialize timer module.
  ret_code_t err_code = app_timer_init();
  APP_ERROR_CHECK(err_code);

  // Create timers.
  err_code = app_timer_create(&m_app_leds_tmr, APP_TIMER_MODE_SINGLE_SHOT, app_leds_timer_handler);
  APP_ERROR_CHECK(err_code);

  err_code = app_timer_create(&m_app_tx_tmr, APP_TIMER_MODE_SINGLE_SHOT, app_tx_timer_handler);
  APP_ERROR_CHECK(err_code);

  err_code = app_timer_create(&m_sound_tmr, APP_TIMER_MODE_REPEATED, sound_timer_handler);
  APP_ERROR_CHECK(err_code);
}

/**@brief Handle events from leds timer.
 *
 * @note Timer handler does not support returning an error code.
 * Errors from app_indication_set() are not propagated.
 *
 * @param[in]   p_context   parameter registered in timer start function.
 */
static void app_leds_timer_handler(void *p_context) {
  //UNUSED_PARAMETER(p_context);
  app_indication_set(m_stable_state);
}


/**@brief Handle events from alert timer.
 *
 * @param[in]   p_context   parameter registered in timer start function.
 */

static void sound_timer_handler(void *p_context) {

  time_stamp += SOUND_TIMER_INTERVAL_SEC;

  UNUSED_PARAMETER(p_context);

  NRF_LOG_INFO("sound_timer_handler  %d", sampling_running);

  if (!sampling_running) {
    start_sound_measurement();
  } else {
    NRF_LOG_INFO("sound_timer_handler ERROR: %d", sampling_running);
    app_indication_set(BSP_INDICATE_SEND_ERROR);
    stop_sound_measurement();
  }
}

/**@brief Function for initializing the nrf log module.
 */
static void log_init(void) {
  ret_code_t err_code = NRF_LOG_INIT(NULL);
  APP_ERROR_CHECK(err_code);

  NRF_LOG_DEFAULT_BACKENDS_INIT();
}

/**@brief Function for initializing power management.
 */
static void power_management_init(void) {
  ret_code_t err_code;
  err_code = nrf_pwr_mgmt_init();
  APP_ERROR_CHECK(err_code);
}

/**@brief Function for handling the idle state (main loop).
 *
 * @details If there is no pending log operation, then sleep until next the next event occurs.
 */
static void idle_state_handle(void) {
  UNUSED_RETURN_VALUE(NRF_LOG_PROCESS());
  nrf_pwr_mgmt_run();
}

static void application_timers_start(void) {
  ret_code_t err_code;
  //err_code = app_timer_start(m_app_timer_id, TIMER_INTERVAL, NULL);
  APP_ERROR_CHECK(err_code);
}
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

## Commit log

2019-06-23 updated calibration
2019-06-23 version of beta
    [calibratie.xlsx]
2019-10-01 arduino mems mic
2019-10-28 working version on esp32
2019-11-03 ready for testing prototype
2019-11-09 working prototype need to fix http upload when offline
    [Tatysound_dummy v0.stl, sounddata copy 2.csv, sounddata copy.csv, sounddata.csv]
2019-12-06 addapting to new sdk
    [part1.stl]
2019-12-06 new hardware schematics
    [bomBLEsoundV1.xlsx]
2019-12-19 optimized db load
    [Body2_simple.stl, dop_usb mini.stl, dop_usbc.stl, sounddata.csv]
2020-01-12 last version
    [dop_usbc.stl]
2020-10-30 added fusion360 file
    [Tatysound_enclosure v6.f3d]

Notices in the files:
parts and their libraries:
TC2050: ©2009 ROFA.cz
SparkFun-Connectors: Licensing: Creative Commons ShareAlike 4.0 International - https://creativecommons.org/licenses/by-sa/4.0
